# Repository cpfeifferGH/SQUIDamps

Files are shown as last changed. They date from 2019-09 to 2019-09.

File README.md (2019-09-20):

# SQUIDamps
Schematic and part list for the SQUIDamp amplifiers/filters described in my PhD thesis: On-scalp MEG using high-Tc SQUIDs - Measuring brain activity with superconducting magnetometers (ISBN 978-91-7905-173-0, Doktorsavhandlingar vid Chalmers tekniska högskola, Ny serie nr 4640, ISSN 0346-718X).

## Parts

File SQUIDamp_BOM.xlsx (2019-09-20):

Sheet: Sheet1
Qty | Value | Device | Package | Parts | Description | MF | MPN | OC_FARNELL | OC_NEWARK | se.farnell | Price/1item | 7 | minQty | Total Price | Price/dev
2 |  | C-EU025-025X050 | C025-025X050 | C9, C16 | CAPACITOR, European symbol |  |  |  |  |  | 0 | 14 | 14 | 0.0 | 0.0
2 | 100u | CPOL-EUB45181A | B45181A | C33, C34 | POLARIZED CAPACITOR, European symbol |  |  | x |  | 1869995 | 41.24 | 14 | 14 | 577.4 | 82.5
2 |  | JP3Q | JP3Q | JP5, JP6 | JUMPER |  |  | x |  | 1022231 | 1.28 | 14 | 20 | 25.6 | 3.7
4 |  | JP4Q | JP4Q | JP1, JP2, JP3, JP4 | JUMPER |  |  | x |  | 1022233 | 1.77 | 28 | 30 | 53.1 | 7.6
4 |  | R-EU_0204/5 | 0204/5 | R8, R9, R16, R26, R27 | RESISTOR, European symbol |  |  |  |  |  | 0 | 28 | 28 | 0.0 | 0.0
2 | 12V | 22-23-2031 | B2+-VH(LF)(SN) | SUPPLY | JST 2pin B2P connector, 3.96mm |  |  | x |  | 9492003 | 1.05 | 14 | 15 | 15.8 | 2.2
1 | 1.6k | R-EU_R0805 | R0805 | R10 | RESISTOR, European symbol |  |  |  |  | 2670961 | 0.253 | 7 | 10 | 2.5 | 0.4
2 | 10 | R-EU_R0805 | R0805 | R13, R14 | RESISTOR, European symbol |  |  |  |  | 2670118 | 9.09 | 14 | 20 | 181.8 | 26.0
6 | 100p | C-EUC0805 | C0805 | C1, C3, C5, C6, C7, C8 | CAPACITOR, European symbol |  |  |  |  | 2320839 | 0.264 | 42 | 50 | 13.2 | 1.9
4 | 10u | C-EUC0805 | C0805 | C10, C11, C12, C15 | CAPACITOR, European symbol |  |  |  |  | 2320856 | 0.624 | 28 | 30 | 18.7 | 2.7
2 | 160 | R-EU_R0805 | R0805 | R5, R7 | RESISTOR, European symbol |  |  |  |  | 2670960 | 0.268 | 14 | 20 | 5.4 | 0.8
1 | 160k | R-EU_R0805 | R0805 | R12 | RESISTOR, European symbol |  |  |  |  | 2670963 | 0.253 | 7 | 10 | 2.5 | 0.4
1 | 16k | R-EU_R0805 | R0805 | R11 | RESISTOR, European symbol |  |  |  |  | 2670962 | 0.261 | 7 | 10 | 2.6 | 0.4
4 | 1k | R-EU_R0805 | R0805 | R1, R2, R15, R22, R23 | RESISTOR, European symbol |  |  |  |  | 2502670 | 0.199 | 28 | 30 | 6.0 | 0.9
2 | 1u | C-EUC0805 | C0805 | C13, C14 | CAPACITOR, European symbol |  |  |  |  | 2320853 | 0.338 | 14 | 15 | 5.1 | 0.7
2 | 22p | C-EUC0805 | C0805 | C4, C31 | CAPACITOR, European symbol |  |  |  |  | 1759195 | 0.175 | 14 | 20 | 3.5 | 0.5
2 | 300 | R-EU_R0805 | R0805 | R3, R24 | RESISTOR, European symbol |  |  |  |  | 2670223 | 9.37 | 14 | 20 | 187.4 | 26.8
2 | 33.2 | R-EU_R0805 | R0805 | R4, R25 | RESISTOR, European symbol |  |  |  |  | 2670083 | 0.718 | 14 | 20 | 14.4 | 2.1
1 | 330 | R-EU_R0805 | R0805 | R6 | RESISTOR, European symbol |  |  |  |  | 2670238 | 9.37 | 7 | 10 | 93.7 | 13.4
2 | 332-02 | 332-02 | 332-02 | IN, OUT | 2 Pin - 2mm Dual Row |  |  | x |  | 1593411 | 0.594 | 14 | 14 | 8.3 | 1.2
6 | 4.7u | C-EUC0805 | C0805 | C25, C26, C27, C28, C29, C30 | CAPACITOR, European symbol |  |  |  |  | 1658237 | 5.93 | 42 | 45 | 266.8 | 38.1
1 | 47p | C-EUC0805 | C0805 | C17 | CAPACITOR, European symbol |  |  |  |  | 1759199 | 0.155 | 7 | 10 | 1.6 | 0.2
1 | 50 | R-EU_0204/5 | 0204/5 | R21 | RESISTOR, European symbol |  |  | x |  | 1903694 | 2.71 | 7 | 7 | 19.0 | 2.7
2 | 5p | C-EUC0805 | C0805 | C2, C32 | CAPACITOR, European symbol |  |  |  |  | 1759184 | 0.342 | 14 | 20 | 6.8 | 1.0
3 | AD797R | AD797R | SO8 | IC1, IC2, IC3 | Ultralow Distortion, Ultralow Noise Op Amp | ALTERA CORPORATION | AD797ARZ | x | 88H0085 | 9426450 | 98.09 | 21 | 21 | 2059.9 | 294.3
61 |  |  |  |  |  |  |  |  |  |  |  |  | SUM: | 3571.0 | 510.1
 |  |  |  |  |  |  |  |  |  | 9708391

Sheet: BOM
Qty | Value | Device | Package | Parts | Description | MPN | OC_FARNELL | SE_FARNELL | Price/p [SEK] | Price/brd [SEK] | Price/7 [SEK]
2 |  | JP3Q | JP3Q | JP5, JP6 | JUMPER |  |  | 1022231 | 1.28 | 2.56 | 17.92
4 |  | JP4Q | JP4Q | JP1, JP2, JP3, JP4 | JUMPER |  |  | 1022233 | 1.77 | 7.08 | 49.56
2 | 10u | L-EU | RFS1113 | R26, R27 | INDUCTOR, European symbol |  |  | 2526883 | 11.02 | 22.04 | 154.28
3 |  | R-EU_0204/5 | 0204/5 | R8, R9, R16 | RESISTOR, European symbol |  |  |  |  | 0.00 | 0.00
2 | 1.6k | R-EU_0204/5 | 0204/5 | R7, R10 | RESISTOR, European symbol |  |  | 9342680 | 0.74 | 1.48 | 10.35
2 | 10 | R-EU_0204/5 | 0204/5 | R13, R14 | RESISTOR, European symbol |  |  | 9342443 | 0.76 | 1.52 | 10.67
6 | 0.1u | C-EU025-025X050 | C025-025X050 | C1, C3, C5, C6, C7, C8 | CAPACITOR, European symbol |  |  | 2395773 | 0.88 | 5.27 | 36.88
2 | 100u | CPOL-EUB45181A | B45181A | C33, C34 | POLARIZED CAPACITOR, European symbol |  |  | 1869995 | 41.24 | 82.48 | 577.36
1 | 10u | C-EU025-025X050 | C025-025X050 | C9 | CAPACITOR, European symbol |  |  | 2525314 | 36.02 | 36.02 | 252.14
1 | 160 | R-EU_0204/5 | 0204/5 | R5 | RESISTOR, European symbol |  |  | 9342672 | 0.73 | 0.73 | 5.13
1 | 160k | R-EU_0204/5 | 0204/5 | R12 | RESISTOR, European symbol |  |  | 9342702 | 0.74 | 0.74 | 5.17
1 | 16k | R-EU_0204/5 | 0204/5 | R11 | RESISTOR, European symbol |  |  | 9342699 | 0.73 | 0.73 | 5.13
5 | 1k | R-EU_0204/5 | 0204/5 | R1, R2, R15, R22, R23 | RESISTOR, European symbol |  |  | 9342400 | 0.76 | 3.81 | 26.67
2 | 1u | C-EU025-025X050 | C025-025X050 | C13 | CAPACITOR, European symbol |  |  | 2112947 | 2.85 | 5.70 | 39.90
2 | 22p | C-EU025-025X050 | C025-025X050 | C4, C31 | CAPACITOR, European symbol |  |  | 1141760 | 1.96 | 3.92 | 27.44
2 | 300 | R-EU_0204/5 | 0204/5 | R3, R24 | RESISTOR, European symbol |  |  | 9342982 | 0.78 | 1.55 | 10.85
2 | 33.2 | R-EU_0204/5 | 0204/5 | R4, R25 | RESISTOR, European symbol |  |  | 9343075 | 0.76 | 1.53 | 10.68
1 | 330 | R-EU_0204/5 | 0204/5 | R6 | RESISTOR, European symbol |  |  | 9343032 | 0.77 | 0.77 | 5.38
2 | 332-02 | 332-02 | 332-02 | IN, OUT | 2 Pin - 2mm Dual Row |  |  | 1593411 | 0.59 | 1.19 | 8.32
6 | 4.7u | CPOL-EUB45181A | B45181A | C25, C26, C27, C28, C29, C30 | POLARIZED CAPACITOR, European symbol |  |  | 9708324 | 7.07 | 42.42 | 296.94
1 | 47p | C-EU025-025X050 | C025-025X050 | C17 | CAPACITOR, European symbol |  |  | 1141762 | 0.65 | 0.65 | 4.52
1 | 50 | R-EU_0204/5 | 0204/5 | R21 | RESISTOR, European symbol |  |  | 1903694 | 2.71 | 2.71 | 18.97
2 | 5p | C-EU025-025X050 | C025-025X050 | C2, C32 | CAPACITOR, European symbol |  |  | 9411640 | 0.37 | 0.74 | 5.21
3 | AD797N | AD797N | DIL08 | IC1, IC2, IC3 | Ultralow Distortion, Ultralow Noise Op Amp | AD797ANZ | 9603778 | 9603778 | 82.77 | 248.31 | 1738.17
2 | B2P-VH | B2P-VH | B2P-VH | +12V, -12V | 2pin connector with 3.96mm pitch |  |  | 9492003 | 1.05 | 2.10 | 14.70
 |  |  |  |  |  |  |  |  | SUM | 476.05 | 3332.34

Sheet: Total Cost
Item | Comment | Price per dev | Priece per 7
Components |  | 476.0 | 3333.0
Board |  | 174.6 | 1221.9
Box |  | 118.0 | 721.0
 | SUM | 768.6 | 5275.9

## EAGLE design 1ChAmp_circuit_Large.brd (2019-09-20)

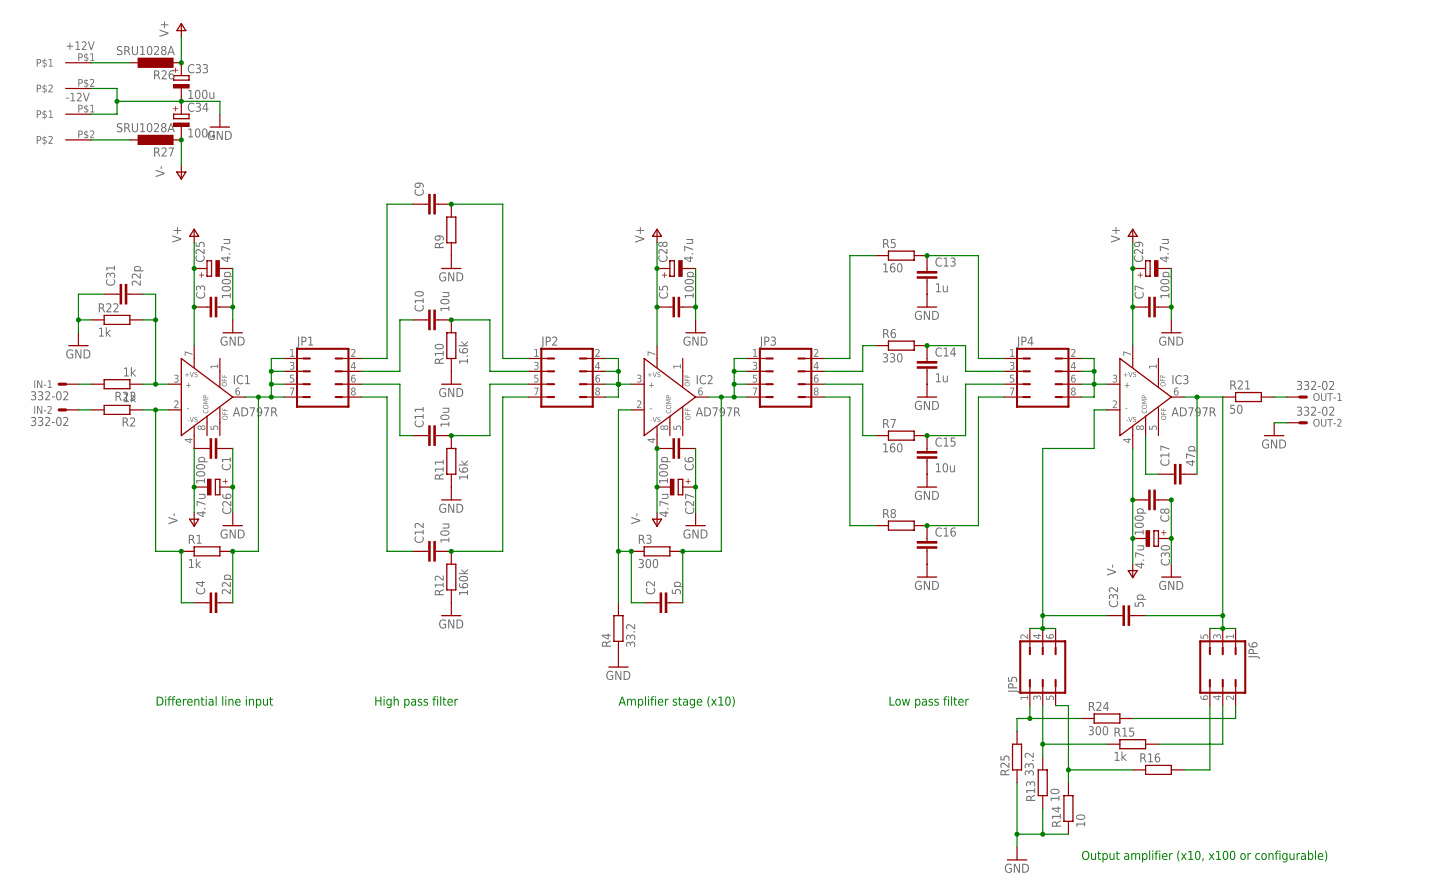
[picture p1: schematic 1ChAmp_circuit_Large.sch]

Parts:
+12V: B2P-VH
-12V: B2P-VH
C1, C3, C5, C6, C7, C8: 100p; C0805
C2, C32: 5p; C0805
C4, C31: 22p; C0805
C9, C16: C-EU025-025X050; C025-025X050
C10, C11, C12, C15: 10u; C0805
C13, C14: 1u; C0805
C17: 47p; C0805
C25, C26, C27, C28, C29, C30: 4.7u; C0805POL
C33, C34: 100u; C0805POL
IC1, IC2, IC3: AD797R; SO8
IN: 332-02
JP1, JP2, JP3, JP4: JP4Q
JP5, JP6: JP3Q
OUT: 332-02
R1, R2, R15, R22, R23: 1k; R0805
R3, R24: 300; R0805
R4, R25: 33.2; R0805
R5, R7: 160; R0805
R6: 330; R0805
R8, R9, R16: R-EU_0204/5; 0204/5
R10: 1.6k; R0805
R11: 16k; R0805
R12: 160k; R0805
R13, R14: 10; R0805
R21: 50; 0204/5
R26, R27: SRU1028A

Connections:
GND: +12V.P$2, -12V.P$1, C1.1, C3.2, C5.2, C6.1, C7.2, C8.1, C13.2, C14.2, C15.2, C16.2, C25.P$1 (-), C26.P$2 (+), C27.P$2 (+), C28.P$1 (-), C29.P$1 (-), C30.P$2 (+), C31.1, C33.P$1 (-), C34.P$2 (+), OUT.2, R4.1, R9.1, R10.1, R11.1, R12.1, R13.1, R14.1, R22.1, R25.1
unnamed: IN.2, R2.2
unnamed: OUT.1, R21.2
unnamed: IN.1, R23.2
unnamed: C31.2, IC1.3 (IN+), R22.2, R23.1
unnamed: JP5.5, R14.2, R16.1
unnamed: C13.1, JP4.1, R5.2
unnamed: C4.1, IC1.2 (IN-), R1.1, R2.1
unnamed: C4.2, IC1.6 (OUT), JP1.1, JP1.3, JP1.5, JP1.7, R1.2
unnamed: C2.1, IC2.2 (IN-), R3.1, R4.2
unnamed: C2.2, IC2.6 (OUT), JP3.1, JP3.3, JP3.5, JP3.7, R3.2
unnamed: C14.1, JP4.3, R6.2
unnamed: C17.1, IC3.8 (COMP)
unnamed: C15.1, JP4.5, R7.2
unnamed: C17.2, C32.2, IC3.6 (OUT), JP6.1, JP6.3, JP6.5, R21.1
unnamed: +12V.P$1, R26.P$1 (1)
unnamed: C16.1, JP4.7, R8.2
unnamed: JP5.3, R13.2, R15.1
unnamed: C9.2, JP2.1, R9.2
unnamed: JP5.1, R24.1, R25.2
unnamed: C10.2, JP2.3, R10.2
unnamed: JP6.2, R24.2
unnamed: C11.2, JP2.5, R11.2
unnamed: JP6.4, R15.2
unnamed: C12.2, JP2.7, R12.2
unnamed: JP6.6, R16.2
unnamed: C32.1, IC3.2 (IN-), JP5.2, JP5.4, JP5.6
unnamed: C9.1, JP1.2
unnamed: C10.1, JP1.4
unnamed: C11.1, JP1.6
unnamed: C12.1, JP1.8
unnamed: IC2.3 (IN+), JP2.2, JP2.4, JP2.6, JP2.8
unnamed: JP3.2, R5.1
unnamed: JP3.4, R6.1
unnamed: JP3.6, R7.1
unnamed: JP3.8, R8.1
unnamed: IC3.3 (IN+), JP4.2, JP4.4, JP4.6, JP4.8
unnamed: -12V.P$2, R27.P$1 (1)
V+: C3.1, C5.1, C7.1, C25.P$2 (+), C28.P$2 (+), C29.P$2 (+), C33.P$2 (+), IC1.7 (+VS), IC2.7 (+VS), IC3.7 (+VS), R26.P$2 (2)
V-: C1.2, C6.2, C8.2, C26.P$1 (-), C27.P$1 (-), C30.P$1 (-), C34.P$1 (-), IC1.4 (-VS), IC2.4 (-VS), IC3.4 (-VS), R27.P$2 (2)

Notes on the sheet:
Differential line input
High pass filter
Amplifier stage (x10)
Low pass filter
Output amplifier (x10, x100 or configurable)

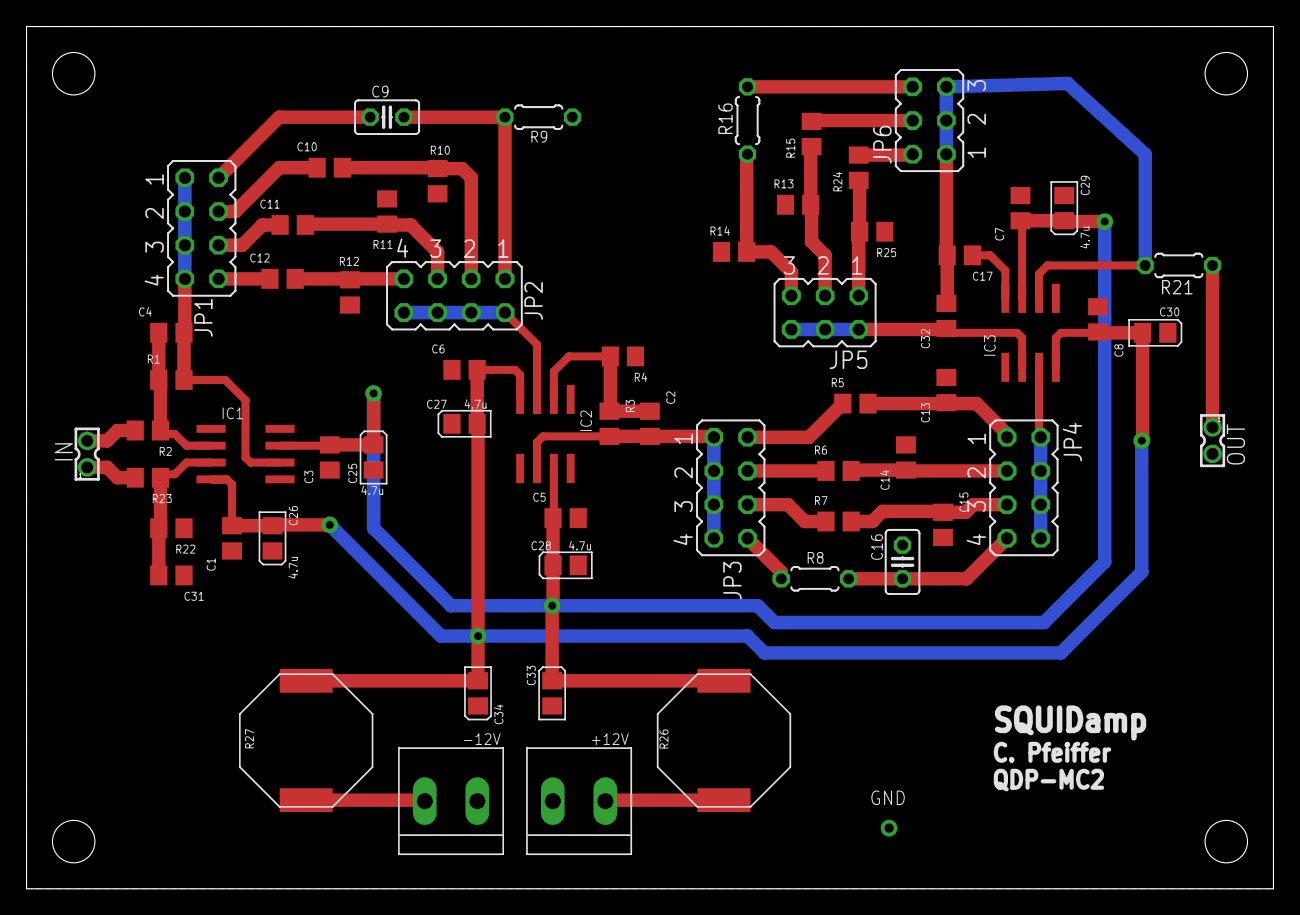
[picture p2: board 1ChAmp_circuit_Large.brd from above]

Board: 2 copper layers, 94.0 x 65.0 mm, 63 parts (0 on the bottom side), 40 nets.
